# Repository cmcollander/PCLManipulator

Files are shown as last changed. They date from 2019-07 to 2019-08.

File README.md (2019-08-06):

# PCLManipulator
An open design for a 2DoF manipulator for 3D point cloud scanning

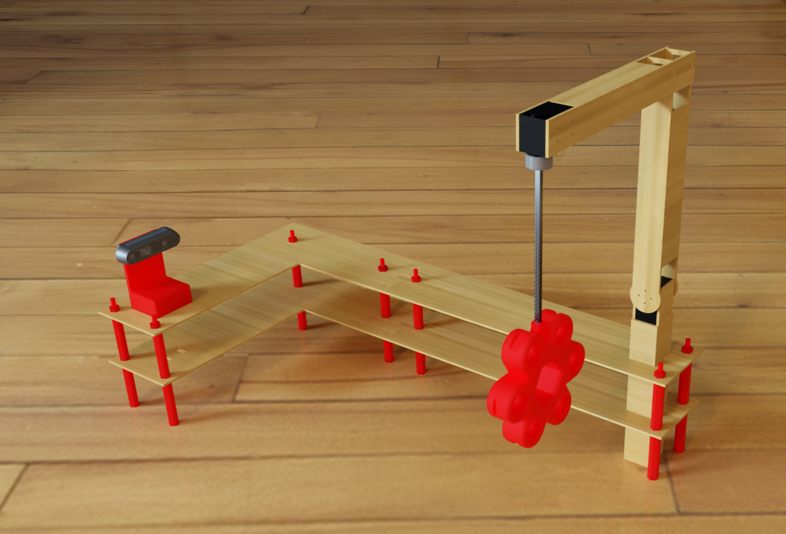
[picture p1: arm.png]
PCLManipulator


This design was created for my PhD research in 3D Point Cloud Analysis. Fusion 360 was used to create a parameterized model capable of many changes. This manipulator can be fully constructed of 3D printed pieces (any plastic will be fine), lasercut wood (3mm baltic birch, in my case), a carbon fiber tube (found at a local hobby shop), 2 Dynamixel XL430 motors, a Realsense D4xx camera, and simple mechanical screws.

A camera in space, for the purposes of observing an object, would need 6DoF (3 for pose, 3 for orientation). For this project, 6DoF would be an unnecesary amount of time, labor, and data. By making the rule that the camera will always face a central origin of the object, we immediately eliminate 3Dof. We can eliminate another by converting to spherical coordinates and constraining the camera to always be a specific distance away from the object. In this final 2DoF representation, we can call the two axes Yaw and Pitch.

## License
MIT License

Copyright (c) 2019 Chris Collander

Permission is hereby granted, free of charge, to any person obtaining a copy
of this software and associated documentation files (the "Software"), to deal
in the Software without restriction, including without limitation the rights
to use, copy, modify, merge, publish, distribute, sublicense, and/or sell
copies of the Software, and to permit persons to whom the Software is
furnished to do so, subject to the following conditions:

The above copyright notice and this permission notice shall be included in all
copies or substantial portions of the Software.

THE SOFTWARE IS PROVIDED "AS IS", WITHOUT WARRANTY OF ANY KIND, EXPRESS OR
IMPLIED, INCLUDING BUT NOT LIMITED TO THE WARRANTIES OF MERCHANTABILITY,
FITNESS FOR A PARTICULAR PURPOSE AND NONINFRINGEMENT. IN NO EVENT SHALL THE
AUTHORS OR COPYRIGHT HOLDERS BE LIABLE FOR ANY CLAIM, DAMAGES OR OTHER
LIABILITY, WHETHER IN AN ACTION OF CONTRACT, TORT OR OTHERWISE, ARISING FROM,
OUT OF OR IN CONNECTION WITH THE SOFTWARE OR THE USE OR OTHER DEALINGS IN THE
SOFTWARE.

## Software

The software is made for a Linux system with the point cloud library (PCL), Realsense SDK 2.0, and Dynamixel SDK installed. Before compilation, you will need to adjust the CMakeLists.txt file to point to your local libraries, as well as adjust the file storage location in main.cpp. This was compiled in Ubuntu 16.04 but I see no reason that it won't work in other Linux distributions as long as the correct libraries are installed and located by CMake.

The software moves the object to a position, obtains the Realsense point cloud, filters the cloud to remove all points outside of a cartesian box, transforms the point cloud to the central origin, and saves the point cloud to external storage. As the PID controllers in the motors cannot make short jumps reliably, the current code moves the two axes randomly in the configuration space, rather than iterating progressively through each possible position. This allows sufficient movement to go to a position within a reasonable margin of error. Despite whatever pose error may be present, the software reads and saves the data as the current position (as opposed to the goal position) which removes the pose error from the collected data. Data points will not be overwritten. Considering the action space is 4096*2048 possible locations, it will take approximately 2 weeks to obtain 90% of the possible positions.

In the future I hope to release code that will fully rotate the object, obtain a streamed point cloud, and use PCL registration to create a fully scanned 3D model of the centralized object. As this does not currently relate to my research projects, it is not at the top of my priority list, but if anybody would like to take on the project let me know and I could provide assistance.

## Hardware

Currently, I will only be releasing the STL files and DXF files for construction, but after I clean up and merge the Fusion 360 projects, I will post those files as well.

For 3D Printing, a Prusa i3 mk3s was used for the pieces, with some pieces being printed in PETG and others in PLA. As relatively little stress will be placed on the pieces, the actual plastic doesn't matter. The only piece that should be printed with high detail is the carbon fiber mount. Ensure the carbon fiber rod does not move in the mount and the mount is secure on the motor with no wiggle room. As the standoffs needed to be specific heights to allow the camera to be facing directly at the origin, these were 3D printed in high quality. If you can find another way to securely ensure the height of each layer, feel free to go that route. This just worked well for us. We even 3D printed the nuts for the standoffs, but I do admit this is unnecessary considering we could have just made a trip to the hardware store. I've included the STL file for them anyways, in case anybody wants to take the same route.

For laser cutting, a Full Spectrum Laser 20x12 Hobby lasercutter was used with RetinaEngrave and CorelDraw. The pieces were all constructed to fit within the bounds of the lasercutter. 3mm baltic birch was used, but if the parameter in Fusion360 for material thickness is changed, there is no reason that a different size of material wouldn't work. For the manipulator itself, simple wood glue and clamps were used for adhesion.

### Building

To build the manipulator you need to lasercut the following files in 3mm wood
* 2x BasePlateVector.dxf
* 2x BaseSupportVector.dxf
* 2x PitchPlateVector.dxf
* 2x PitchSupportVector.dxf
* 2x YawPlateVector.dxf
* 2x YawSupportVector.dxf
* 2x Platform1Vector.dxf
* 2x Platform2Vector.dxf

The following pieces should be 3D printed
* 1x CameraSupport.stl
* 1x CarbonFiberMotorMount.stl
* 14x Standoff.stl
* 7x Nut.stl (optional)

The following pieces should be purchased
* 1x Realsense D4xx Camera
* 2x Dynamixel XL430 motors (and any necessary cables, boards, power supplies, and USB adapters to get these working for your system)
* 1x Carbon Fiber 5mm-OD square tube: https://www.hobbytown.com/midwest-carbon-fiber-square-tube-.196-od-x-.118-id-x-40-mid5854/p28823
* Any screws necessary for the build. I happened to have what I needed on hand, so I didn't keep track of exactly what I used. I'd recommend picking up one of the assortment kits of various M3 and M5 metal screws.

Let me know if you have any questions. I don't know how many adjustments or changes I'd be willing my make to the model, as it suits my needs in the current form, but if you have any feel free to submit a pull request and we can change it!

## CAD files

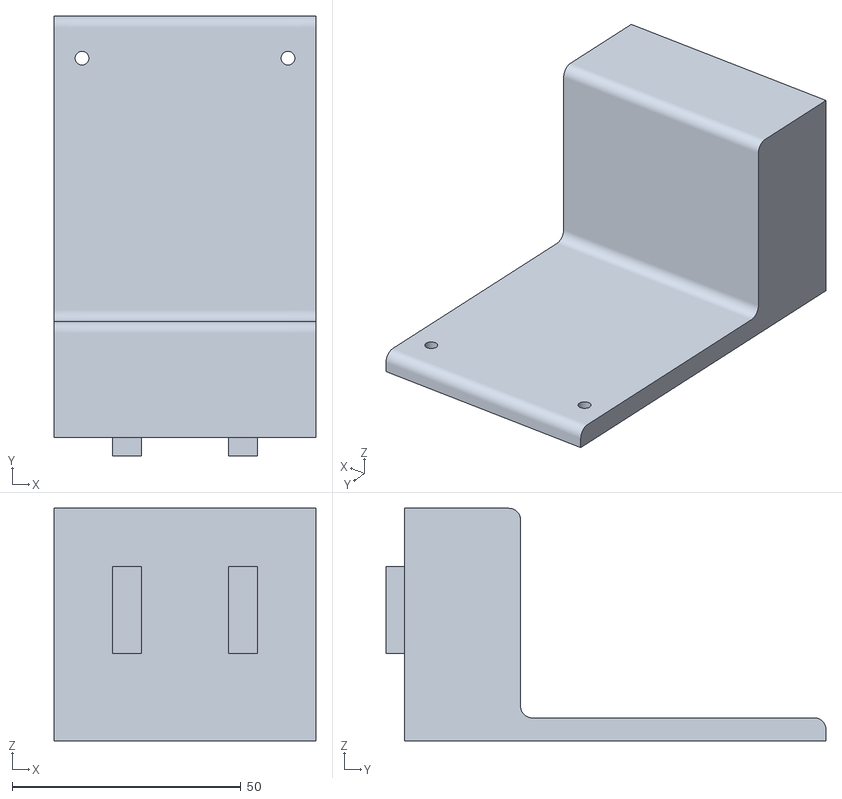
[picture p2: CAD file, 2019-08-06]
CameraSupport.stl
57.2 x 96.1 x 50.8

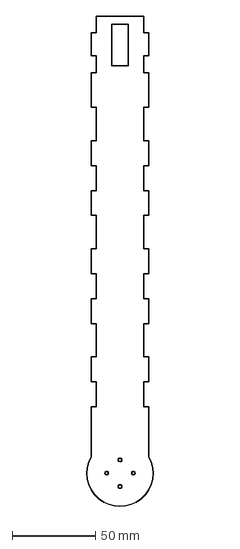
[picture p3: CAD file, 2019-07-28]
hardware/PitchPlateVector.dxf
44.3 x 296.6 mm

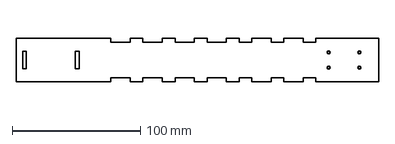
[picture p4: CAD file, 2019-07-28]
hardware/YawPlateVector.dxf
283.1 x 34.0 mm

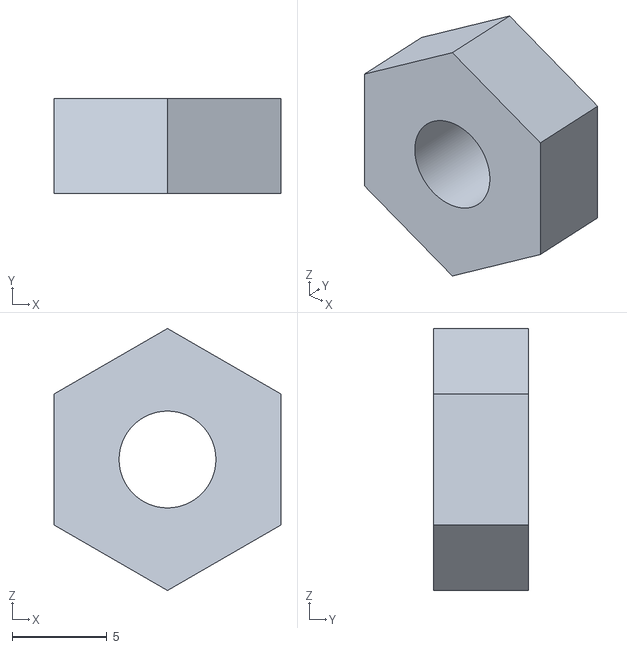
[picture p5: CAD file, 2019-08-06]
StandoffNut.stl
12.0 x 5.00 x 13.9

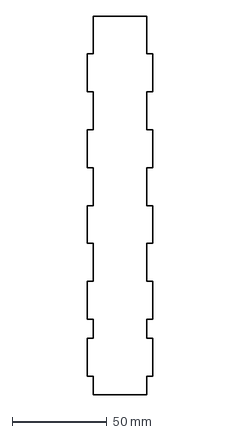
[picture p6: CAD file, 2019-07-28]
hardware/BaseSupportVector.dxf
34.6 x 200.0 mm

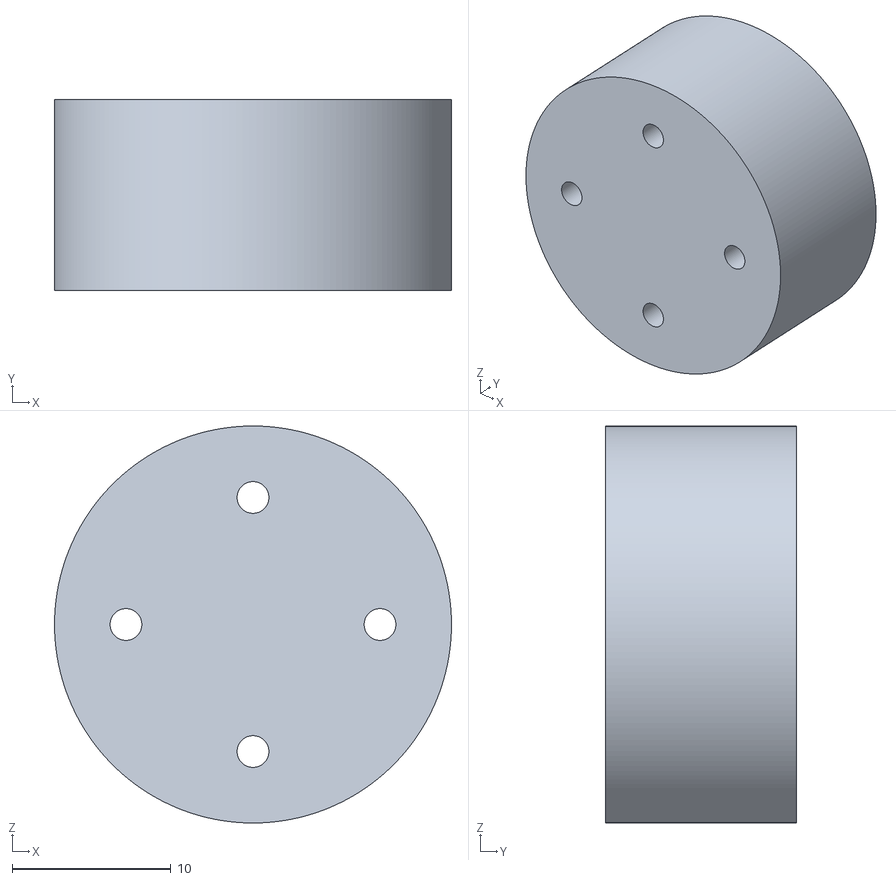
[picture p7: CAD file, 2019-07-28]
hardware/CarbonFiberMotorMount.stl
25.0 x 12.0 x 25.0

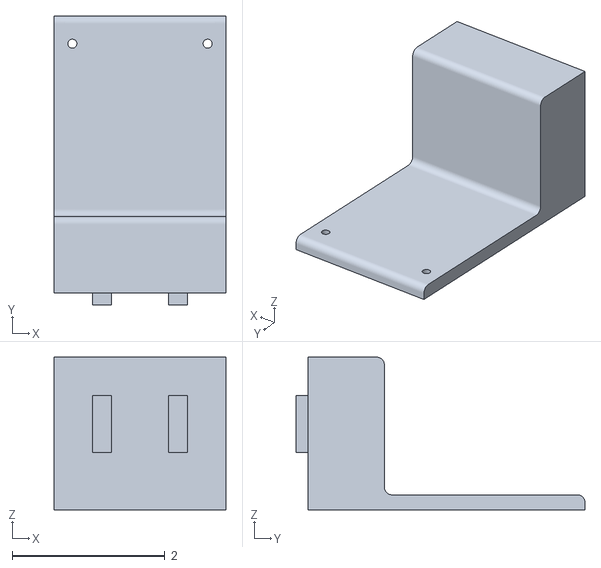
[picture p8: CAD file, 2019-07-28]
hardware/RealsenseMount.stl
2.25 x 3.78 x 2.00

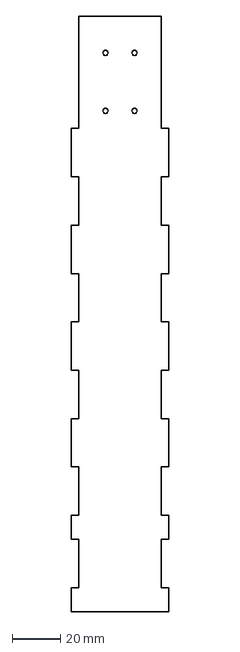
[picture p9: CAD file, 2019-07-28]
hardware/VasePlateVector.dxf
40.2 x 246.5 mm

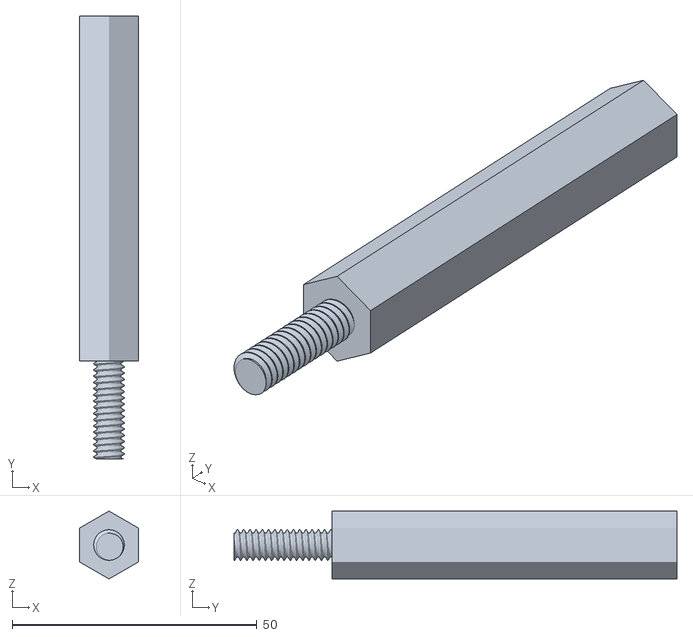
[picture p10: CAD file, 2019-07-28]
hardware/Standoff.stl
12.0 x 90.4 x 13.9

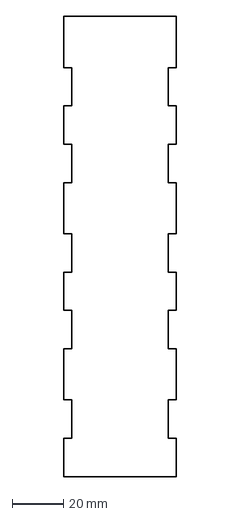
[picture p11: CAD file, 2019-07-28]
hardware/PitchSupportVector.dxf
44.1 x 180.0 mm

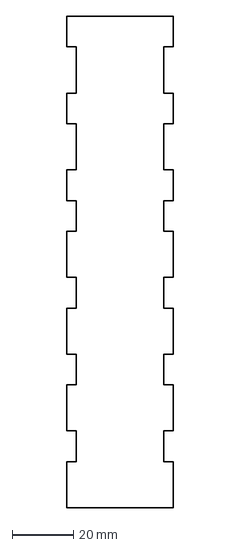
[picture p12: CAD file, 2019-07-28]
hardware/YawSupportVector.dxf
34.6 x 160.0 mm

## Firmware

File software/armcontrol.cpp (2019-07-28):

// PCLManipulator
// July 2019, Chris Collander

/*
MIT License

Copyright (c) 2019 Chris Collander

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
THE SOFTWARE IS PROVIDED "AS IS", WITHOUT WARRANTY OF ANY KIND, EXPRESS OR
IMPLIED, INCLUDING BUT NOT LIMITED TO THE WARRANTIES OF MERCHANTABILITY,
FITNESS FOR A PARTICULAR PURPOSE AND NONINFRINGEMENT. IN NO EVENT SHALL THE
AUTHORS OR COPYRIGHT HOLDERS BE LIABLE FOR ANY CLAIM, DAMAGES OR OTHER
LIABILITY, WHETHER IN AN ACTION OF CONTRACT, TORT OR OTHERWISE, ARISING FROM,
OUT OF OR IN CONNECTION WITH THE SOFTWARE OR THE USE OR OTHER DEALINGS IN THE
SOFTWARE.
*/

#include <iostream>
#include <string>
#include <sstream>
#include <cmath>
#include <chrono>
#include <thread>
#include <random>
#include <unistd.h>

#include "dynamixel_sdk.h" 

#include <librealsense2/rs.hpp>

#include <pcl/point_types.h>
#include <pcl/filters/crop_box.h>
#include <pcl/io/pcd_io.h>
#include <pcl/visualization/pcl_visualizer.h>

// Set to true to visualize the point cloud after every frame
#define VISUALIZE false

// Dynamixel communication parameters
#define PROTOCOL_VERSION 2.0
#define YAW_ID 2
#define PITCH_ID 1
#define BAUDRATE 57600
#define DEVICENAME "/dev/ttyUSB0"

// Dynamixel command parameters
#define TORQUE_ENABLE 1
#define TORQUE_DISABLE 0
#define LED_ENABLE 1
#define LED_DISABLE 0
#define DXL_MOVING_STATUS_THRESHOLD 20
#define DXL_MOVING_STATUS_TIME_THRESHOLD_SECONDS 12
#define ESC_ASCII_VALUE 0x1b

// Predefined positional motor values 
#define YAW_MINIMUM_POSITION_VALUE 0
#define YAW_MAXIMUM_POSITION_VALUE 4095
#define PITCH_MINIMUM_POSITION_VALUE 1024
#define PITCH_MAXIMUM_POSITION_VALUE 3072
#define CENTER_POSITION_VALUE 2048
#define PITCH_OFFSET 0
#define YAW_OFFSET 0

// Register addresses for Dynamixel commands
#define ADDR_GOAL_POSITION 116
#define ADDR_MAX_POSIT_LIM 48
#define ADDR_MIN_POSIT_LIM 52
#define ADDR_TORQUE_ENABLE 64
#define ADDR_PROFILE_ACCEL 108
#define ADDR_PROFILE_VELOC 112
#define ADDR_PRESENT_POSIT 132
#define ADDR_OPERATING_MOD 11
#define ADDR_HOMING_OFFSET 20
#define ADDR_DRIVE_MODE 10
#define ADDR_LED 65
#define ADDR_HARDWARE_ERROR 70

// Transform and Filter dimensions
#define OBJECT_RADIUS 0.1
#define X_ORIGIN 0.011
#define Y_ORIGIN 0.0
#define Z_ORIGIN 0.58

using namespace std;
using namespace rs2;

// Global variables! I know, I hate them too....
dynamixel::PortHandler *portHandler = dynamixel::PortHandler::getPortHandler(DEVICENAME);
dynamixel::PacketHandler *packetHandler = dynamixel::PacketHandler::getPacketHandler(PROTOCOL_VERSION);
uint8_t dxl_error = 0;
int32_t yaw_present_position = 0;
int32_t pitch_present_position = 0;

// Randomness, Uniform, Unbiased
random_device seeder;
mt19937 rng(seeder());
uniform_int_distribution<int> yaw_gen(YAW_MINIMUM_POSITION_VALUE, YAW_MAXIMUM_POSITION_VALUE);
uniform_int_distribution<int> pitch_gen(PITCH_MINIMUM_POSITION_VALUE, PITCH_MAXIMUM_POSITION_VALUE);

// Global PCL Variables for reduced calculations
pcl::CropBox<pcl::PointXYZ> boxFilter;
Eigen::Affine3f transformer;

// Easy function to see if a file already exists
bool fileexists(const string &filename) {
    return access(filename.c_str(), 0)==0;
}

// Determine if yaw and pitch are within minimum and maximum values
bool withinBounds(int yaw, int pitch) {
    bool test1 = yaw >= YAW_MINIMUM_POSITION_VALUE;
    bool test2 = yaw <= YAW_MAXIMUM_POSITION_VALUE;
    bool test3 = pitch >= PITCH_MINIMUM_POSITION_VALUE;
    bool test4 = pitch <= PITCH_MAXIMUM_POSITION_VALUE;
    return test1 && test2 && test3 && test4;
}

// Convert an angle in degrees into a motor position index
int angle2index(float angle) {
    const float index_min = 1024;
    const float index_max = 3072;
    const float angle_min = -180;
    const float angle_max = 180;
    const float index = (angle - angle_min) * (index_max - index_min) / (angle_max - angle_min) + index_min;
    return int(index+0.5);
}

// Convert a motor position index into degrees
float index2angle(int index) {
    const float index_min = 1024;
    const float index_max = 3072;
    const float angle_min = -180;
    const float angle_max = 180;
    return (index - index_min) * (angle_max - angle_min) / (index_max - index_min) + angle_min;
}

// Move the manipulator to a specific yaw and pitch (by positional index). 
// Will stop when either position delta is less than DXL_MOVING_STATUS_THRESHOLD
// Or (assuming it can't get close enough to the new position)
// Will time out after DXL_MOVING_STATUS_TIME_THRESHOLD_SECONDS
// Either way, will save actual positions to global variables ???_present_position
void moveTo(int yaw, int pitch) {
    cout<<"Move: {"<<yaw<<","<<pitch<<"}"<<flush;

    packetHandler->write4ByteTxRx(portHandler, YAW_ID, ADDR_GOAL_POSITION, yaw, &dxl_error);
    packetHandler->write4ByteTxRx(portHandler, PITCH_ID, ADDR_GOAL_POSITION, pitch, &dxl_error);
    auto start = chrono::steady_clock::now();
    do { // Wait until both motors are at the correct locations (based on DXL_MOVING_STATUS_THRESHOLD). Possible timeout
      packetHandler->read4ByteTxRx(portHandler, YAW_ID, ADDR_PRESENT_POSIT, (uint32_t*)&yaw_present_position, &dxl_error);
      packetHandler->read4ByteTxRx(portHandler, PITCH_ID, ADDR_PRESENT_POSIT, (uint32_t*)&pitch_present_position, &dxl_error);
    } while(chrono::duration_cast<chrono::seconds>(chrono::steady_clock::now() - start).count()<DXL_MOVING_STATUS_TIME_THRESHOLD_SECONDS && ((abs(yaw-yaw_present_position)>DXL_MOVING_STATUS_THRESHOLD) || (abs(pitch-pitch_present_position)>DXL_MOVING_STATUS_THRESHOLD)));
    cout<<" ---> {"<<yaw_present_position<<","<<pitch_present_position<<"}"<<flush;
}

// Check the hardware error status registers of the motors for any problems
void checkHardwareStatus() {
    int yaw_status = -1;
    int pitch_status = -1;
    packetHandler->read4ByteTxRx(portHandler, YAW_ID, ADDR_HARDWARE_ERROR, (uint32_t*)&yaw_status, &dxl_error);
    packetHandler->read4ByteTxRx(portHandler, PITCH_ID, ADDR_HARDWARE_ERROR, (uint32_t*)&pitch_status, &dxl_error);
    yaw_status   &= 0xF;
    pitch_status &= 0xF;
    cout<<"Hardware Status:\tYAW="<<yaw_status<<"\tPITCH="<<pitch_status<<endl;
}

// Will convert realsense points to a PCL ptr
pcl::PointCloud<pcl::PointXYZ>::Ptr points_to_pcl(const points& points) {
    pcl::PointCloud<pcl::PointXYZ>::Ptr cloud(new pcl::PointCloud<pcl::PointXYZ>);

    auto sp = points.get_profile().as<video_stream_profile>();
    cloud->width = sp.width();
    cloud->height = sp.height();
    cloud->is_dense = false;
    cloud->points.resize(points.size());
    auto ptr = points.get_vertices();
    for (auto& p : cloud->points) {
        p.x = ptr->x;
        p.y = ptr->y;
        p.z = ptr->z;
        ptr++;
    }
    return cloud;
}

// Will allow visualization of a cloud, returning from the function when the window is closed
void visualize(pcl::PointCloud<pcl::PointXYZ>::Ptr &pcl_cloud) {
    pcl::visualization::PCLVisualizer::Ptr viewer (new pcl::visualization::PCLVisualizer ("3D Viewer"));
    viewer->setBackgroundColor (0, 0, 0);
    viewer->addPointCloud<pcl::PointXYZ> (pcl_cloud, "cloud");
    viewer->setPointCloudRenderingProperties (pcl::visualization::PCL_VISUALIZER_POINT_SIZE, 1, "cloud");
    viewer->addCoordinateSystem (1.0);
    viewer->initCameraParameters ();
    while (!viewer->wasStopped ()) {
        viewer->spinOnce (100);
        this_thread::sleep_for(chrono::milliseconds(100));
    }
}

// Obtain a point cloud from the realsense
// Handles translation and rotation to center the object,
// And filtering to remove things that are not the object.
// Saves to a file based on the name parameter
void getPointCloudWithName(pipeline &pipe, points &pts, pointcloud &pc, string name) {
    pcl::PointCloud<pcl::PointXYZ>::Ptr input_cloud (new pcl::PointCloud<pcl::PointXYZ> ());
    pcl::PointCloud<pcl::PointXYZ>::Ptr transformed_cloud (new pcl::PointCloud<pcl::PointXYZ> ());
    pcl::PointCloud<pcl::PointXYZ>::Ptr filtered_cloud (new pcl::PointCloud<pcl::PointXYZ> ());

    // Get our point cloud
    auto frames = pipe.wait_for_frames();
    auto color = frames.get_color_frame();
    auto depth = frames.get_depth_frame();
    pts = pc.calculate(depth);
    pc.map_to(color);
    input_cloud = points_to_pcl(pts);
    
    // Translate and filter
    transformPointCloud(*input_cloud, *transformed_cloud, transformer);
    boxFilter.setInputCloud(transformed_cloud);
    boxFilter.filter(*filtered_cloud);

    // Save and visualize
    pcl::io::savePCDFileASCII(name.c_str(), *filtered_cloud);
    if(VISUALIZE)
        visualize(filtered_cloud);
}

// Reboot the motors and establish correct parameters
void reboot() {
    cout<<"Pre-Reboot"<<endl;
    checkHardwareStatus();

    // Reboot both motors
    packetHandler->reboot(portHandler, YAW_ID, &dxl_error);
    packetHandler->reboot(portHandler, PITCH_ID, &dxl_error);

    // Wait 5 seconds for reboot
    this_thread::sleep_until(chrono::system_clock::now() + chrono::seconds(5));
    cout<<"Post-Reboot"<<endl;
    checkHardwareStatus();

    // Set positional offsets
    packetHandler->write4ByteTxRx(portHandler, YAW_ID, ADDR_HOMING_OFFSET, YAW_OFFSET, &dxl_error);
    packetHandler->write4ByteTxRx(portHandler, PITCH_ID, ADDR_HOMING_OFFSET, PITCH_OFFSET, &dxl_error);

    // Set drive and operating modes
    packetHandler->write1ByteTxRx(portHandler, YAW_ID, ADDR_DRIVE_MODE, 0, &dxl_error);
    packetHandler->write1ByteTxRx(portHandler, PITCH_ID, ADDR_DRIVE_MODE, 0, &dxl_error);
    packetHandler->write1ByteTxRx(portHandler, YAW_ID, ADDR_OPERATING_MOD, 3, &dxl_error);
    packetHandler->write1ByteTxRx(portHandler, PITCH_ID, ADDR_OPERATING_MOD, 3, &dxl_error);    

    // Set Yaw Profile
    packetHandler->write4ByteTxRx(portHandler, YAW_ID, ADDR_PROFILE_ACCEL, 25, &dxl_error);
    packetHandler->write4ByteTxRx(portHandler, YAW_ID, ADDR_PROFILE_VELOC, 25, &dxl_error);

    // Set Pitch Profile
    packetHandler->write4ByteTxRx(portHandler, PITCH_ID, ADDR_PROFILE_ACCEL, 25, &dxl_error);
    packetHandler->write4ByteTxRx(portHandler, PITCH_ID, ADDR_PROFILE_VELOC, 25, &dxl_error);

    // Set Minimum and Maximum Yaw Values
    packetHandler->write4ByteTxRx(portHandler, YAW_ID, ADDR_MAX_POSIT_LIM, YAW_MAXIMUM_POSITION_VALUE, &dxl_error);
    packetHandler->write4ByteTxRx(portHandler, YAW_ID, ADDR_MIN_POSIT_LIM, YAW_MINIMUM_POSITION_VALUE, &dxl_error);

    // Set Minimum and Maximum Pitch Values
    packetHandler->write4ByteTxRx(portHandler, PITCH_ID, ADDR_MAX_POSIT_LIM, PITCH_MAXIMUM_POSITION_VALUE, &dxl_error);
    packetHandler->write4ByteTxRx(portHandler, PITCH_ID, ADDR_MIN_POSIT_LIM, PITCH_MINIMUM_POSITION_VALUE, &dxl_error);

    // Enable Torque
    packetHandler->write1ByteTxRx(portHandler, YAW_ID, ADDR_TORQUE_ENABLE, TORQUE_ENABLE, &dxl_error);
    packetHandler->write1ByteTxRx(portHandler, PITCH_ID, ADDR_TORQUE_ENABLE, TORQUE_ENABLE, &dxl_error);

    // Center both motors
    moveTo(CENTER_POSITION_VALUE, CENTER_POSITION_VALUE);
    cout<<endl;
}

// bundles together the getPointCloudWithName and moveTo functions for abstraction
// Given a yaw and pitch (indexes) go to that position and obtain, transform, filter, and save the pointcluod.
// Will NOT overwrite or even try to obtain PC for a position that it already has
void moveAndSave(int yaw, int pitch, pipeline &pipe, points &pts, pointcloud &pc) {
    stringstream ss;
    moveTo(yaw, pitch);
    ss << "/media/cmc1078xx/ExternalDrive1/data/" << yaw_present_position << "_" << pitch_present_position <<".pcd";
    if(!fileexists(ss.str())) {
        cout<<"\tFile: NEW"<<endl;
        getPointCloudWithName(pipe, pts, pc, ss.str());
    } else if(!withinBounds(yaw_present_position,pitch_present_position)) {
        cout<<"\tERROR: OUT OF BOUNDS! Rebooting motors..."<<endl;
        reboot();
    } else
        cout<<"\tFile: EXISTS"<<endl;
}
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

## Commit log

2019-07-28 Added software and updated license
    [BaseSupportVector.dxf, CarbonFiberMotorMount.stl, PitchPlateVector.dxf, PitchSupportVector.dxf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]
2019-08-06 Adding StandoffNut.stl
    Just in case others want to print them instead of purchasing.
    [StandoffNut.stl]
